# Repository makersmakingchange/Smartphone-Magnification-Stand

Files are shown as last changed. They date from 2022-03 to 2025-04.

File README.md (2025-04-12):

# Smartphone Magnification Stand

## Overview

This inexpensive 3D printed smartphone stand will allow for a smartphone to be held up while it is being used as a magnifier.  This phone stand may be beneficial to someone with visual impairment that requires text to be enlarged or better contrasted to its surroundings in order to read it. The phone stand is designed to hold the user's smartphone up high enough from the page that the camera on the back of the user's phone can fully focus. The inspiration for the design of this phone stand is credited to the Visor Smartphone Stand.

## Compatibility

This phone stand was designed to fit the width of most smart phones. The phone stand is indented to fit smartphones that range from 60mm - 90mm in width.

## Usage

This phone stand is intended to be paired with a magnification app that one can find in the app store on their phone. The phone stand holds a phone parallel to the surface it is placed on and is easy to slide around. The user will place the phone in the phone stand, and place the phone stand on top of the sheet of paper they are trying to read from. A magnification app will allow the user to choose magnification, contrast, and lighting options  that will help them most clearly see the page. The user will then hold down the page with one hand and move the phone stand and phone with the other as needed to read across the page.

## Skills Required

3D printing

## 3D Printing

The design prints in PLA with no supports. A 3D print STL can be found at the top of this page in Design Files.

## Attribution

 - Kerilyn Kennedy - Makers Making Change

<!-- ABOUT MMC START -->
## About Makers Making Change
[Makers Making Change Logo](https://www.makersmakingchange.com/)

Makers Making Change is a program of [Neil Squire](https://www.neilsquire.ca/), a Canadian non-profit that uses technology, knowledge, and passion to empower people with disabilities.

Makers Making Change leverages the capacity of community based Makers, Disability Professionals and Volunteers to develop and deliver affordable Open Source Assistive Technologies.

 - Website: [www.MakersMakingChange.com](https://www.makersmakingchange.com/)
 - GitHub: [makersmakingchange](https://github.com/makersmakingchange)
 - Bluesky: [@makersmakingchange.bsky.social](https://bsky.app/profile/makersmakingchange.bsky.social)
 - Instagram: [@makersmakingchange](https://www.instagram.com/makersmakingchange)
 - Facebook: [makersmakechange](https://www.facebook.com/makersmakechange)
 - LinkedIn: [Neil Squire Society](https://www.linkedin.com/company/neil-squire-society/)
 - Thingiverse: [makersmakingchange](https://www.thingiverse.com/makersmakingchange/about)
 - Printables: [MakersMakingChange](https://www.printables.com/@MakersMakingChange)

### Contact Us
For technical questions, to get involved, or to share your experience we encourage you to [visit our website](https://www.makersmakingchange.com/) or [contact us](https://www.makersmakingchange.com/s/contact).
<!-- ABOUT MMC END -->

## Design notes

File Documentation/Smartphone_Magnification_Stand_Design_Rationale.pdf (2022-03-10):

V1.0 FEB 2022

## Smartphone Magnification Stand

## DESIGN RATIONALE

© 2021 by <Author>.
This work is licensed under the CC BY SA 4.0 License: http://creativecommons.org/licenses/by-sa/4.0
Files available at <Replace with MMC Library Link> | Page 1 of 5

### Introduction

This inexpensive 3D printed smartphone stand will allow for a smartphone to be held up while it is being used as a magnifier. This phone stand may be beneficial to someone with visual impairment that requires text to be enlarged or better contrasted to its surroundings in order to read it. The phone stand is designed to hold the user’s smartphone up high enough from the page that the camera on the back of the user’s phone can fully focus.

### Research

In order to determine how tall or how wide to make the phone stand, it was required to research different widths and minimum focus distances for various smart phones. Many phones were researched, and below is an excerpt of what could be considered the smallest and largest width of popular smartphones:

| Name | Brand | Width (mm)
Smallest Width Phone | iPhone SE | Apple | 67.3
| iPhone SE with case | Apple | 79.2
Largest Width Phone | iPhone 13 Pro Max | Apple | 78.1
| iPhone 13 Pro Max with Case | Apple | 86.7

The table below is an excerpt of the various popular smartphones and their minimum focus distances. It was found that most minimum focus distances were 80mm or less.

Name | Brand | Minimum Focus Distance (mm)
iPhone 13 Pro Max | Apple | 20
iPhone 12 Pro Max | Apple | 80
Google Pixel 6 Pro | Google | 80
Samsung Galaxy A52 | Samsung | 50
Samsung Galaxy A71 | Samsung | 50
Samsung Galaxy S20 Ultra | Samsung | 153

## DESIGN RATIONALE

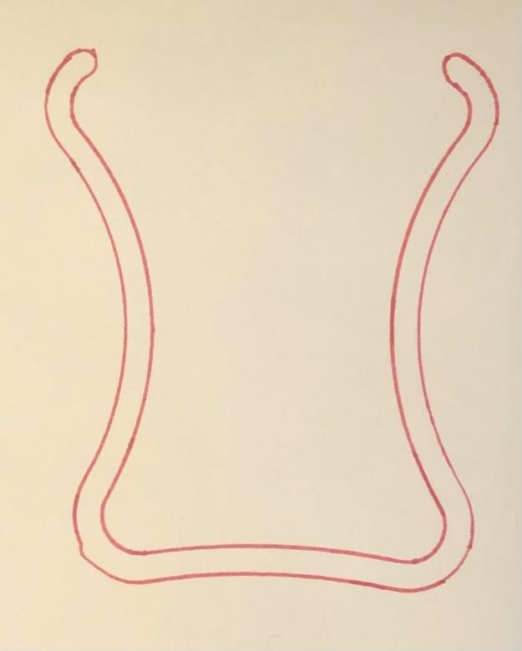
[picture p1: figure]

Files available at <Replace with MMC Library Link> | Page 2 of 5

Commercial Option:

Name | Vendor | Cost | Link
Visor Stand | Visor App | $41.26 | Smartphone Stand — Visor – Magnifier App for iPhone and Android (visorapp.net) (https://www.visorapp.net/magnifiershop/smartphonestand)

### Design Considerations

The goal of this project was to develop an open-source version of a simple stand for a smartphone so it can be used as a magnifier. A key requirement of the phone stand was that it must be able to accommodate a variety of smartphones that are different widths and may have different minimum focus distances for their cameras.

### Ideation

Idea 1: The first design was inspired from the Visor Stand. This design is very simple and requires no assembly.

## DESIGN RATIONALE

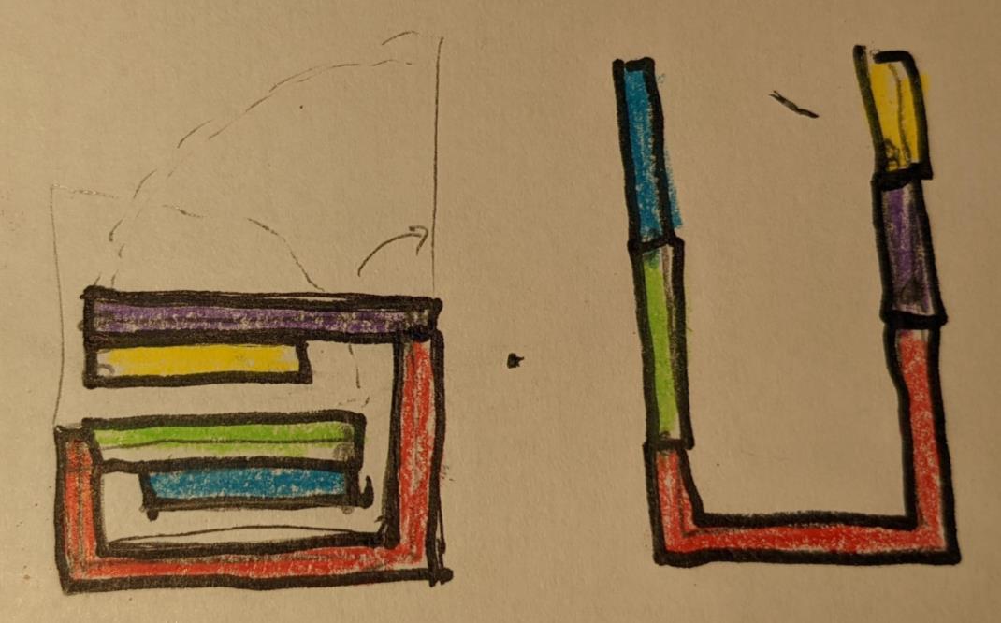
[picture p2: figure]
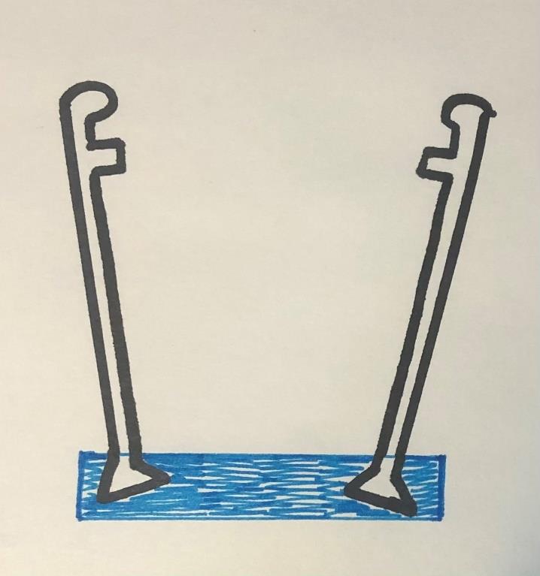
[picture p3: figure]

Files available at <Replace with MMC Library Link> | Page 3 of 5

Idea 2: The second idea was to design a phone stand that can fold so it could be more portable. The sides of the phone stand are longer than the base, so it would be required that the sides themselves would also have to fold in. The pieces would have to be able to fold opened and lock at a given angle to hold the phone.

Idea 3: The third idea was to design a phone stand that could be disassembled so it could be more portable. It is required that the phone stand must be able to be put together quickly for efficient use.

## DESIGN RATIONALE

Files available at <Replace with MMC Library Link> | Page 4 of 5

### Prototyping

It was decided to continue developing a phone stand based on the first idea as it is the simplest and there is no assembly required. Many prototypes were made in order to determine which design would best work for the majority of popular smartphones. Some of the factors that varied over the course of the prototypes included: how tall the phone stand was, its depth, how thick the walls were, how wide the opening was, and how curved it was.

Height: The height of the phone stand was chosen in order to try and accommodate the minimum focus distance of most smartphones. It was found that most smartphones had a minimum focus distance of 80mm or less. Making the phone stand much taller would not only increase print time, but it would make the phone stand bulkier, as well as obstruct the view of the camera more. Blocking the view of the camera can be solved by sliding back the phone stand away from the camera, but doing this too much makes the phone and phone stand unstable.

Depth: The depth of the phone stand was chosen based on the trade off between ensuring that the phone stand was stable, without increasing the print time too much. It can also be noted that if the phone stand is too thick, it might obstruct the view of the camera. Through prototyping, it was found that the taller the phone stand required a thicker base to achieve the same level of stability.

Wall Thickness: The wall thickness of the phone stand was selected based on the trade off between strength and flexibility of the phone stand. It was found that if the walls were too thin, they became fragile and more likely to break. If the walls were too thick, the phone stand would exert a greater force on the phone and would sometimes press in the buttons on the side of the phone.

Opening Width: The size of the opening width of the phone stand was selected to ensure that most different width smartphones could use the stand. The opening had to be small enough that the smallest smartphones would not fall out, but wide enough that when the phone stand is pulled apart to accommodate bigger phones, that it would not break.

Curvature: The curvature of the phone stand was selected as it allowed for the phone to be held up, as well as contributed to the phone’s flexibility.

### Testing

Each prototype was tested by placing different sized phones in the phone stand. It was through testing that different discoveries were made with regards to the height, depth, wall thickness, opening width, and curvature, mentioned previously. Another discovery that was made through the process of testing was that many of the phone stands broke at the bottom corners when the phone stand was pulled apart too far. Upon further investigation, it was determined that the corners were breaking across the infill and not at the existing outer shells. This observation then led to increasing the number of shells in order

## DESIGN RATIONALE

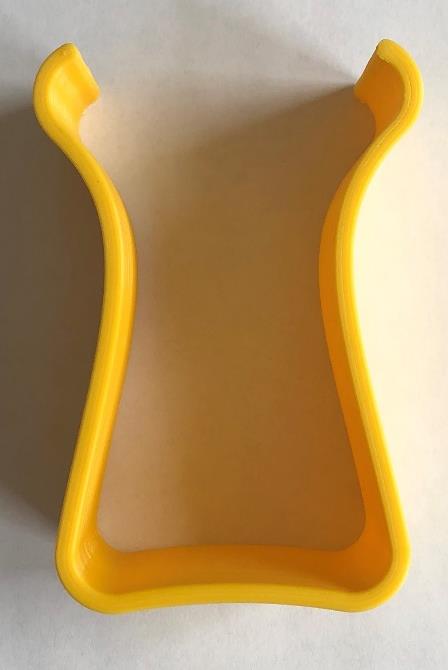
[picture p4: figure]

Files available at <Replace with MMC Library Link> | Page 5 of 5

to eliminate the need for infill. This allowed for the phone stand to become stronger and actually improve its flexibility.

### Final Design

The final design was inspired from the Visor Stand. This design is very simple and requires no assembly.

### Opportunities for Improvement

- Portability: to design a phone stand that can fold or dismantle in order for it to be easier to transport.
- Flexibility: Designing a phone stand that is not required to be in a constant strain to accommodate different sized phones.
- Improving balance: Increasing stability in the phone stand without blocking the view of the camera of the smartphone.

### Credited Resources Used In Development

https://www.visorapp.net/magnifiershop/smartphonestand

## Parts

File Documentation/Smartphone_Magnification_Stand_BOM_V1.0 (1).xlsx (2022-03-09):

Device: Smartphone Magnification Stand |  | Total Cost | Total Print time (hr) | Total filament (g)
Version: V1.0 | Date Created: FEB 2022 | $1.00 | 2.67 | 40
Commercial Parts:
Part type (Electrical. Mechanical, Sanitization, ect) | Part Name | Quantity Needed | Pkg Quantity | Price per package | Price per Unit | Price for qty needed | Link
 |  | 0 | 1 | $0.00 | $0.00 | $0.00
 |  | 0 | 1 | $0.00 | $0.00 | $0.00
 |  | 0 | 1 | $0.00 | $0.00 | $0.00
3D Printed Parts ESTIMATED PRICING USING 1KG ROLL COST: | $25.00
Part | Description | Quantity Needed | TOTAL Mass (g) | Estimated Price | Print Time (Min) | Link
Smartphone Stand |  |  | 40 | $1.00 | 160
 |  |  |  | $0.00
 |  |  |  | $0.00
 |  |  |  | $0.00
 |  |  |  | $0.00
 |  |  | Total Print Cost: | $1.00
Tools for Assembly
Alternatives (if there are other sources for some parts link them below)
Part and description | Link

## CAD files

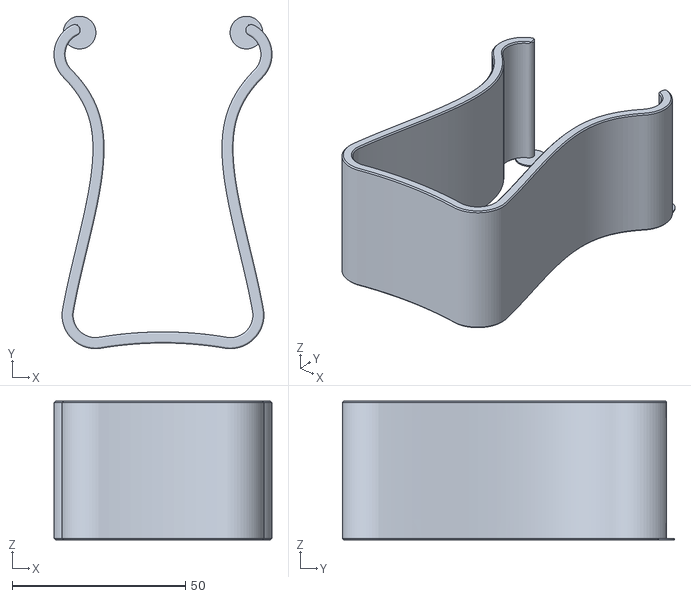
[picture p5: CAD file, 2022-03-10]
3D Print Files/Smartphone Magnification Stand.stl
62.9 x 95.9 x 40.0

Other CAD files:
Design Files/Smartphone Magnification Stand.step
Design Files/Smartphone Magnification Stand.f3d

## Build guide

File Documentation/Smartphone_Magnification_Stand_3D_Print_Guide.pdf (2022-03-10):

V1.0 | Feb 2022

## Smartphone Magnifier Stand

## 3D PRINTING GUIDE

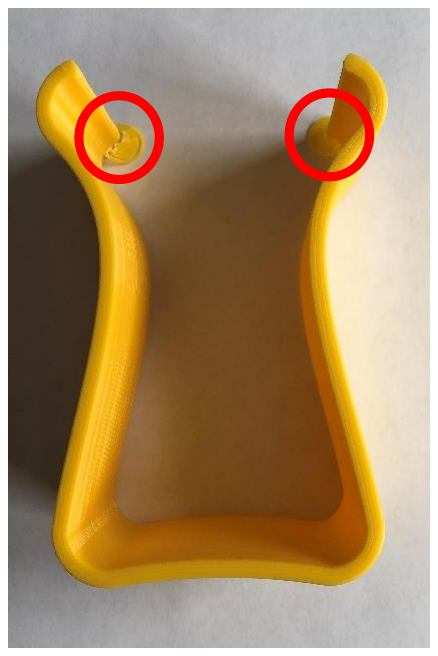
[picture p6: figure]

© 2021 by <Author>.
This work is licensed under the CC BY SA 4.0 License: http://creativecommons.org/licenses/by-sa/4.0
Files available at <Replace with MMC Library Link> | Page 1 of 2

### 3D Printing Summary

Metrics | Smartphone Stand
Total Print Time (min) | 2:24
Total Number of Components | 1
Typical Total Mass (g) | 40
Typical Number of Print Setups | 1

### 3D Printing Settings

Print File Name | Qty | Total Print Time (hr:min) | Mass (g) | Infill (%) | Support (Y/N) | Layer Height/ Nozzle Diameter (mm) | Notes (orientation, special settings, etc)
Smartphone_ Magnification _Stand.stl | 1 | 2:24 | 40 | 20 | N | 0.2/0.4 | Print the phone stand with 4 perimeters so that it is solid, and no infill is required. Print in orientation given in STL.

### Post-Processing

Use a pair of scissors or a hobby knife to remove the small circles located at the top of the phone stand.

V1.0 | Feb 2022

## Smartphone Magnifier Stand

## 3D PRINTING GUIDE

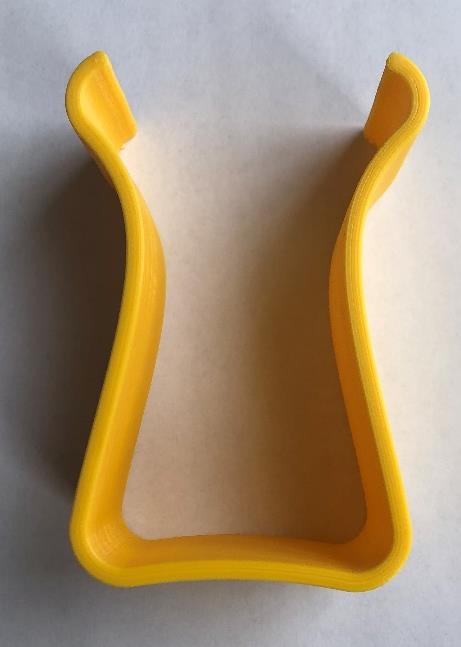
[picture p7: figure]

© 2021 by <Author>.
This work is licensed under the CC BY SA 4.0 License: http://creativecommons.org/licenses/by-sa/4.0
Files available at <Replace with MMC Library Link> | Page 2 of 2

### Customization Options

The user can request that the device be printed in multiple colours and printed with custom text or markings.

### Example of Quality Print

Below is a picture of what print quality is expected from printing the device.

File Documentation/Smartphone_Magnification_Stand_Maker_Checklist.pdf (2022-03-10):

V1.0 | FEB 2022

## Smartphone Magnification Stand

## MAKER CHECKLIST

© 2021 by <Author>.
This work is licensed under the CC BY SA 4.0 License: http://creativecommons.org/licenses/by-sa/4.0
Files available at <Replace with MMC Library Link> | Page 1 of 1

## Maker To Do List

Determine the cost of materials and relay this cost to the user before printing to ensure the requester is comfortable with the price.
Ask the requester if they want any customizations to the device (e.g., color, text).
Print the device.
Deliver the device and User Quick Guide to the requestor.

## Items to Give to User

User Quick Guide
Smartphone Magnification Stand

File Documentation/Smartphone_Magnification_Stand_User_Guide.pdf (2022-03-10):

V1.0 | FEB 2022

## Smartphone Magnification Stand

## USER QUICK GUIDE

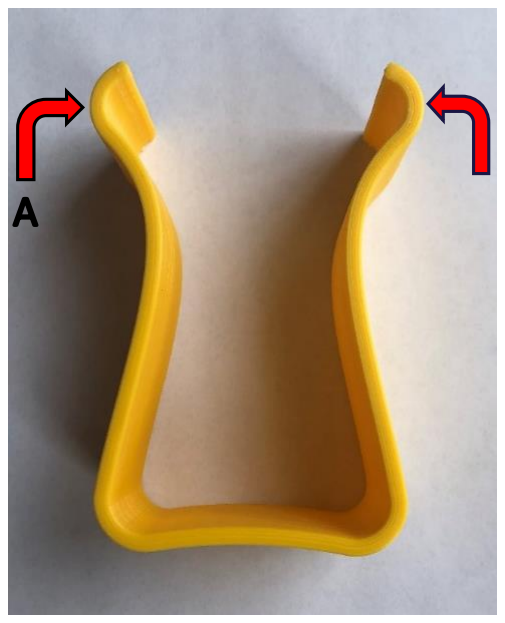
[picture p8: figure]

© 2021 by Neil Squire. (https://neilsquire.ca/)

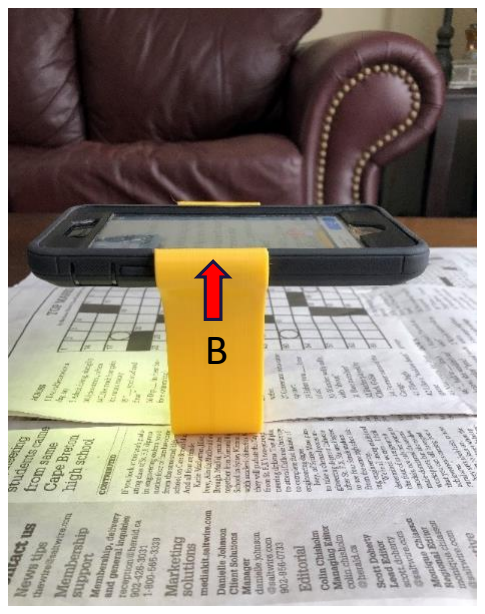
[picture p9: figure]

This work is licensed under the CC BY SA 4.0 License: http://creativecommons.org/licenses/by-sa/4.0
Files available at <MMC Project Library Link> | Page 1 of 2

© 2021 by <Author>. This work is licensed under the CC BY SA 4.0 License: http://creativecommons.org/licenses/by-sa/4.0
Files available at <Replace with MMC Library Link> | Page 1 of 2

### Introduction

This inexpensive 3D printed Smartphone Magnification Stand will allow for a smartphone to be held up while it is being used as a magnifier. This phone stand may be beneficial to someone with visual impairment that requires text to be enlarged or better contrasted to its surroundings in order to read it. The phone stand is designed to hold the user’s smartphone up high enough from the page that the camera on the back of the user’s phone can fully focus.

### Features

The phone stand consists of one 3D printed piece. The top of the phone stand is curved and is used to hold up the phone parallel to the surface the user is trying to read from [A]. These edges can be pulled apart in order to accommodate most sized smartphones [B].

### Usage

This phone stand is intended to be paired with a magnification app that one can find in the app store on their phone. The phone stand will hold up a phone parallel to whatever surface the stand is placed on and is easy to slide around. The user will place the phone in the phone stand and then place the phone stand on top of the sheet of paper they are trying to read from. A magnification app will allow the user to choose magnification, contrast, and lighting options that will help them most clearly see the page. The user will then hold down the page with one hand and move the phone stand and phone with the other as needed to read across the page.

V1.0 | FEB 2022

## Smartphone Magnification Stand

## USER QUICK GUIDE

© 2021 by Neil Squire. (https://neilsquire.ca/)
This work is licensed under the CC BY SA 4.0 License: http://creativecommons.org/licenses/by-sa/4.0
Files available at <MMC Project Library Link> | Page 2 of 2

© 2021 by <Author>. This work is licensed under the CC BY SA 4.0 License: http://creativecommons.org/licenses/by-sa/4.0
Files available at <Replace with MMC Library Link> | Page 2 of 2

### Compatibility

This phone stand was designed to fit the width of most smart phones. The phone stand is indented to fit smartphones that range from 60 mm - 90 mm in width.

### Specifications

Mass (g) | Dimensions (mm)
X | Y | Z
40 | 57 | 88 | 50

### Cleaning

The Smartphone Magnification Stand can be wiped down with sanitizing cleaners. Do not wash the phone stand in high heat as it may cause it to melt or break. (i.e., do not put it in the dishwasher, the washing machine, or soak it in hot water).
